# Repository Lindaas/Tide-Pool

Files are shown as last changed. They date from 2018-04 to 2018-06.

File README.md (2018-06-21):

# Tide-Pool
**This repository contains the code to run the tide pool
for the marine lab biology group.**

## Table of Contents
1. [Description](#Description)
2. [Installation](#Installation)
3. [Code Discussion](#Code-Discussion)
4. [Credit](#credit)

## Description
This code controls the pumping system for both the tide pool and the stingray
lagoon. There are currently two pumps that when one is on, it empties the tank
it is in filling the other tank.

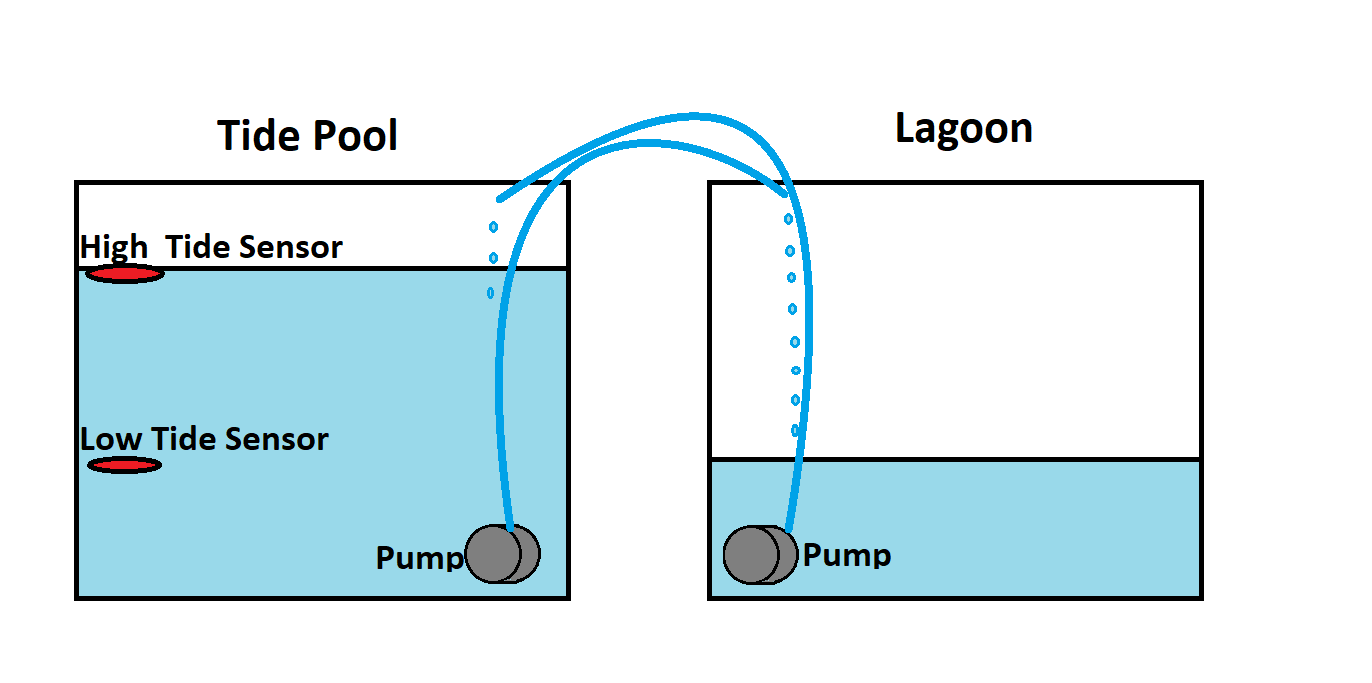
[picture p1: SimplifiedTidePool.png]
Simplified Tide Pool Diagram


Currently, the tide pool and lagoon oscillate between high and low tide every six and a half hours. The system wants the tide pool to be at high tide when the lagoon is at low tide and vice versa. When the [Arduino program](TidePoolLCD/TidePoolLCD.ino) starts, the tide pool fills with water from the lagoon. This filling by turning the pump off for five minutes and then turning it on for the next five minutes repeats until the high tide sensor is triggered. If for some reason the water level decreases, the pump will fill again until the high tide sensor is on. After six and a half hours passed, the system then will pump water from the tide pool into the lagoon until the tide pool's low tide sensor is triggered. After six and a half hours pass, the pump to fill the tide pool turns on and this tidal system repeats.

This system is connected to hardware that connects it to Wi-Fi called the Adafruit Huzzah ESP8266 Breakout Board. This system gets the height values from the ultrasonic sensor that the Arduino records. These values are then sent to Adafruit io, a free online tool. The levels are recorded every three seconds and are kept for a month and can be found at [Adafruit IO Online Dashboard](https://io.adafruit.com/anonymousAlligator/dashboards/ultrasonicsensordashboard). If the Arduino stops, the data isn't sent to Adafruit io and an email notification is sent within 30 minutes.

The schematic for the current system looks like the below image:
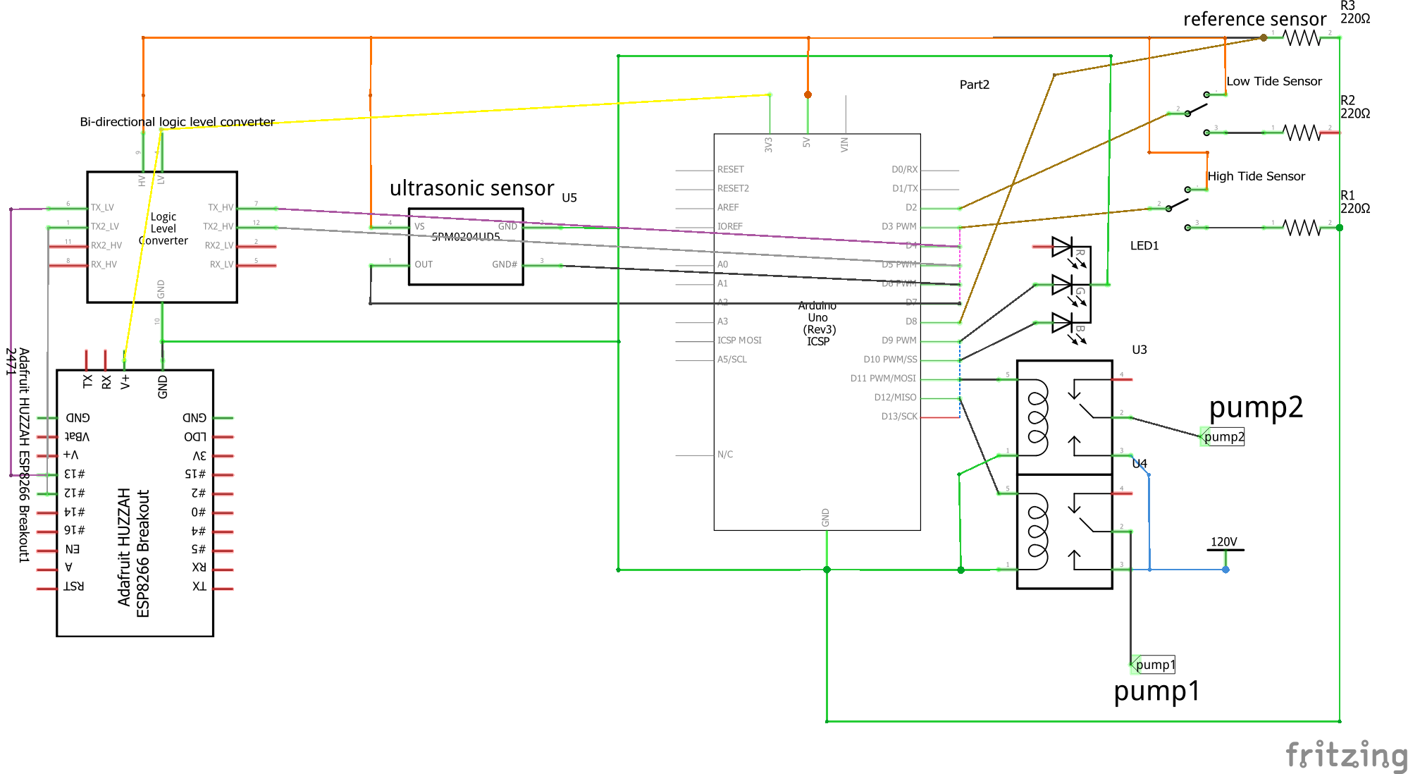
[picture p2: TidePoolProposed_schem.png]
Tide Pool Schematic


**Soon to be implemented** the tidal data will be pulled from online and will mimic the tidal predictions from Kiptopeke, VA.

## Installation
1. Download the [Arduino IDE](https://www.arduino.cc/en/Main/Software?) or preferred Arduino editor.
2. Clone the repository `git clone https://github.com/meyerpa/Tide-Pool.git`
3. Upload https://github.com/meyerpa/Tide-Pool/blob/master/TidePoolLCD/TidePoolLCD.ino to an Arduino.
4. [Create an Adafruit IO Account](https://accounts.adafruit.com/users/sign_up). If need help figuring out how use it, follow the [adafruit io getting started guide](https://learn.adafruit.com/mqtt-adafruit-io-and-you/getting-started-on-adafruit-io)
5. Update `IO_USERNAME`, `IO_KEY`, `WIFI_SSID` (Wi-Fi Network Name), and `WIFI_PASS` (Wi-Fi Password), in `ESP8266/config.h` then upload https://github.com/meyerpa/Tide-Pool/tree/master/ESP8266 to the Adafruit ESP8266 Huzzah Board.
6. Connect the hardware as shown in the below schematic above Installation.

## Components
**SunFounder 2 Channel Relay**

Image of the 2 Channel Relay

The relay allows the Arduino Uno to switch the pumps on and off as necessary.  The Arduino is a low voltage and low amperage system and cannot supply enough power to operate the pumps.  The relay functions like a switch and you should hear a “click” when a pump switches on or off, which also turn one of two red lights located on the rear of the device.
[*URL*](http://www.amazon.com/SunFounder-Channel-Shield-Arduino-Raspberry/dp/B00E0NTPP4/ref=sr_1_2?ie=UTF8&qid=1436551285&sr=8-2&keywords=relay+arduino)

The Arduino and the relay should be connected as follows:

|Arduino	| Relay |
|---------|-------|
| GND	    | GND   |
| 5V	    |	VCC   |
| 11    	| IN1   |
|12	      | IN2   |

**Arduino Uno - Microcontroller**

Image of the Arduino Uno

The Arduino acts like the brain of the system.  It talks to the relay to turn the pumps on and off based on the code that is programmed into the controller.  Only 14 of the pins (labeled: GND, 5V, 3.3V, 2, 3, 4, 5, 6, 7, 8, 9, 10, 11, and 12) should be in use.
The USB cord is used to upload code from a computer to the Arduino and may remain connected to the board.  The last connection to the board is the power supply (looks similar to a phone charger), which will have to power the Arduino at all, time and the charger should have a red light to indicate that it is on.  The Arduino should have a green light to indicate that it is receiving power that is located on the opposite side as the USB port.
[*URL*](http://www.amazon.com/Atmega328p-Atmega16u2-Version-Board-Arduino/dp/B00SF28U7A/ref=sr_1_8?ie=UTF8&qid=1436553628&sr=8-8&keywords=arduino)

**Grove Seeed RGB LCD**

Image of RGB LCD

This LCD (Liquid Crystal Display) shows the system’s current state—filling or draining. It also shows whether the high or low tide bobbers are triggered. If the bobbers are both triggered, the system is in an error state.
[*URL*](http://wiki.seeedstudio.com/Grove-LCD_RGB_Backlight/)

**Grove Seeed Base Shield V2**

Image of Grove Seeed Base Shield V2

This shield allows the RGB LCD to easily communicate with the Arduino.
[*URL*](http://wiki.seeedstudio.com/Base_Shield_V2/)

**Ultrasonic Sensor HC-SR04**

Image of Ultrasonic Sensor

This sensor can read the exact water level. This sensor reads in the exact tidal level. This sensor sends the tidal level readings to the Wi-Fi ESP8266 chip.
[*URL*](https://www.sparkfun.com/products/13959)

**Bi-directional Logic Converter**

Image of Bi-directional Logic Converter

This chip converts the Arduino’s 5 Volt digital output pins to a 3 Volt level able to be read by the Wi-Fi chip. This is because the Wi-Fi chip operates on a 3 Volt logic level, while the Arduino operates on a 5 Volt logic level. If the Arduino is incorrectly connected to the Wi-Fi chip without the logic converter, the Wi-Fi chip could break.
[*URL*](https://www.sparkfun.com/products/12009)

**Wi-Fi Chip (Adafruit ESP8266 Huzzah Breakout Board)**

Image of Adafruit ESP8266 Huzzah Breakout Board

This chip is connected to a wireless network. This enables the project to send the tidal readings to an online source. The current online source the tidal data is pushed to is Adafruit io. This online source accepts data every three seconds, and will send an email after thirty minutes if the system is halted. This chip gets readings from the Arduino via a serial connection on pin 12 (receiving RX) and pin 13 (transmitting TX) and sends that information to the Adafruit io system to be logged for a month.
[*URL*](https://learn.adafruit.com/adafruit-huzzah-esp8266-breakout/overview)

**High Tide Switch/Bobber**

Image of High Tide Switch/Bobber

This switch tells whether the tide is high or low. This bobber switches the fill pump off after the pump has been on for the minimum five-minute time.
[*URL*](https://www.amazon.com/uxcell-Pieces-ZP4510-Vertical-Switches/dp/B00FHAEBIA/ref=sr_1_2?ie=UTF8&qid=1529595162&sr=8-2&keywords=arduino+float+switch)

**Low Tide Switch/Bobber**

Image of Low Tide Switch/Bobber

This switch tells whether the tide is high or low. This bobber switches the drain pump off after the pump has been on for the minimum five-minute time.
[*URL*](https://www.amazon.com/uxcell-Pieces-ZP4510-Vertical-Switches/dp/B00FHAEBIA/ref=sr_1_2?ie=UTF8&qid=1529595162&sr=8-2&keywords=arduino+float+switch)

**Saltwater Pump (2)**

Image of Saltwater Pump

These two pumps do not operate at the same head and the head “velocity” will very over time between the two they pump at different rates.  These pumps are connected to an outlet, which turns on the pumps through the relay. This means that even though the pumps may look like they are plugged in, the outlet may be “off”.
[*URL*](https://www.drsfostersmith.com/product/prod_display.cfm?c=3578+4587+21413&pcatid=21413)

**Waterproof Hobby Box**

Image of Waterproof Hobby Box

This is a box that keeps the electrical components dry.  There were some issues (minor shock) due to the hobby box not being waterproof and corrosive saltwater vapor.  Make sure that if the box is opened that the cords that are fed into the box rest between the jell sealant and that the box clasps are properly fastened.  If a replacement is needed make sure to purchase a large one.
[*URL*](http://www.amazon.com/Weatherproof-Outdoor-Electrical-Connection-Enclosure/dp/B006EUHRK6/ref=sr_1_fkmr3_1?ie=UTF8&qid=1431288296&sr=8-1-fkmr3&keywords=waterproof+electrical+hobby+box)

## Code Discussion 
The code has two components:
1. [The  Arduino part that controls the motors](https://github.com/meyerpa/Tide-Pool/blob/master/TidePoolLCD/TidePoolLCD.ino)
2. [The Wi-Fi Chip Part that uploads the tidal level](https://github.com/meyerpa/Tide-Pool/tree/master/ESP8266)

The Arduino is running this current code.

The code requires input from sensors. There are two sensors to detect extreme tidal level. One sensor detects high tide and the other sensor detects low tide. The tide switches from high to low and vice versa every 6.5 hours.

The Arduino controls the pumps through a relay. The Arduino will either be in a state of filling or draining the tide pool. The fill and drain will continue until the high or low tide sensors are toggled, respectively. When the tide pool is filling, the fill pump will either be one or off. The pump is initially off for five minutes and then will turn on for the next five minutes. The following five minutes the pump will be off. This pattern continues until the high tide bobber is toggled on. A similar pattern happens with the drain pump until the low tide bobber is toggled on.

This system functions by itself filling and draining the tide pool. But there is an additional system to send the tide level online, so the system can be monitored. This additional system has a ultrasonic sensor to detect the exact water (tidal) level. This sensor observes the tidal level and sends the level online by serially communicating to the Wi-Fi chip which sends the level to the [Adafruit IO Online Feed](https://io.adafruit.com/anonymousAlligator/feeds/ultrasonicsensor).

## Credit 
[Dr. Steve Lindaas](mailto:lindaas@mnstate.edu),
[Paige Meyer](mailto:paigemey7@gmail.com), or
[Benjamin LeMay](benjaminlemay@protonmail.com)

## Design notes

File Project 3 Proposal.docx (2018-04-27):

# Project 3

Paige Meyer

# Objective

I first propose to update the tide pool’s pumping system in the marine lab to make it safer. The way I would like to make the pumping system more safe is to have the pumps grounded when off as opposed to the current high voltage when off, and ungrounded. I will also like to make the system more understandable to diagnose by adding a LCD screen to state whether the left tank is tidally filling, still, or falling. I also propose to add either shrink-wrap or electrical tape to the uninsulated wire connections to avoid unintentional short circuits in the future.

I secondly propose to use ultrasonic sensors to the pump system. These ultrasonic sensors will be located high above the tank, to avoid splash failures. These sensitive sensors will enable a more precise control of the water level. This precise control will enable the tide pool to mock Chesapeake Bay’s tides.

The third part of the project will be to connect a Wi-Fi module to the pumping system; this will enable the pool to access the up-to-date Chesapeake tide from an online database. This query will allow realistic tidal simulations in our current marine lab.

The fourth and last part of the project I propose to do is to have the system send an email to the marine lab group when a sensor fails, to inform them of the failure and correct the failure. I would also like to create a webpage that shows the current tide level in the marine lab alongside the Chesapeake Bay actual tide levels.

# Project Design

## Schematic

The initial, starting schematic is shown in Figure 1.

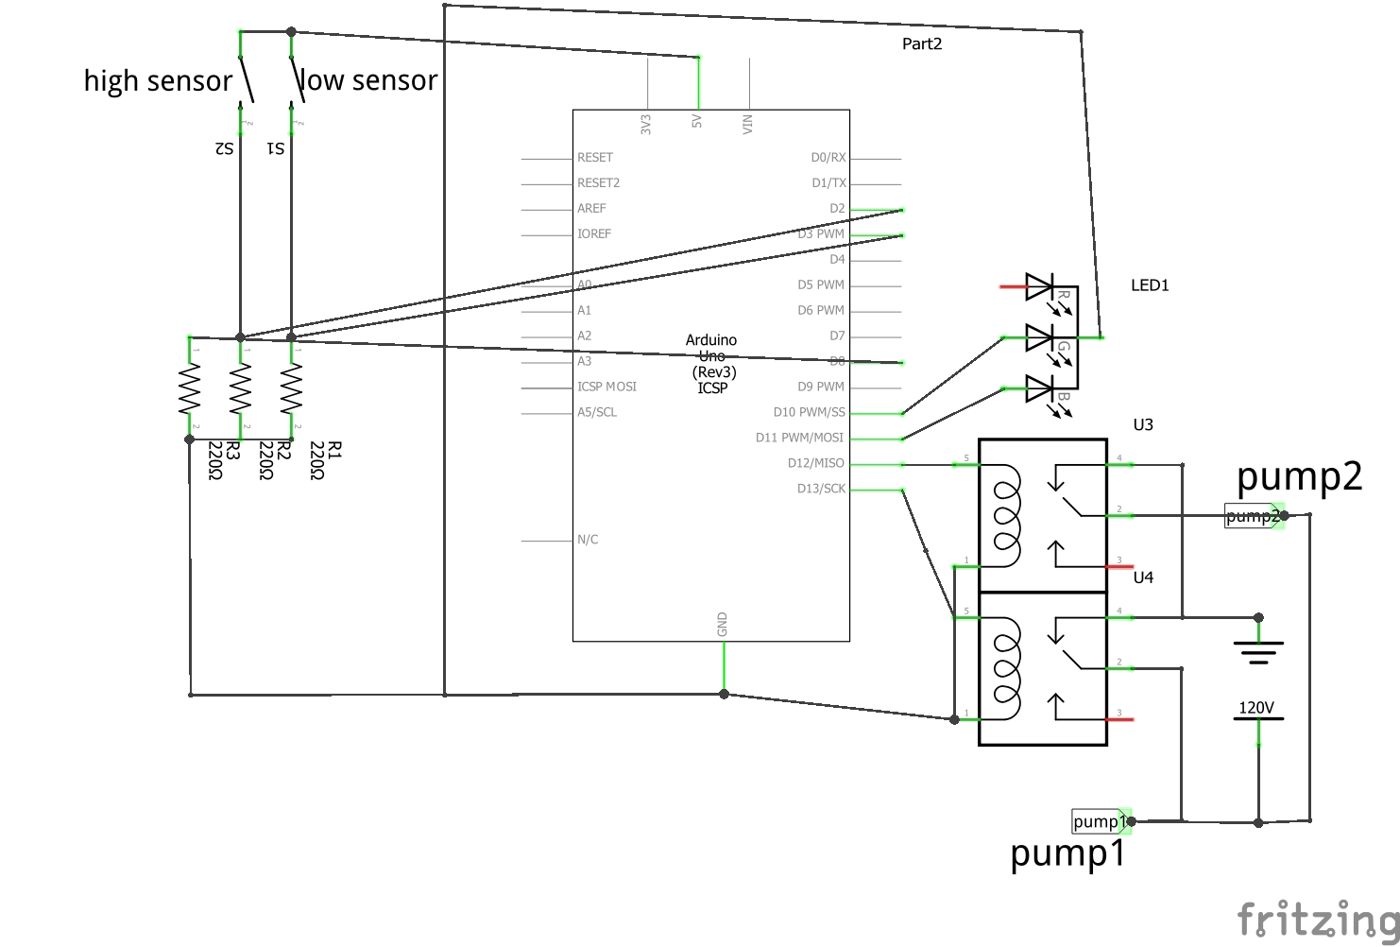
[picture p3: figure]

Figure 1-Initial Starting Schematic

My proposed schematic would look like Figure 2.

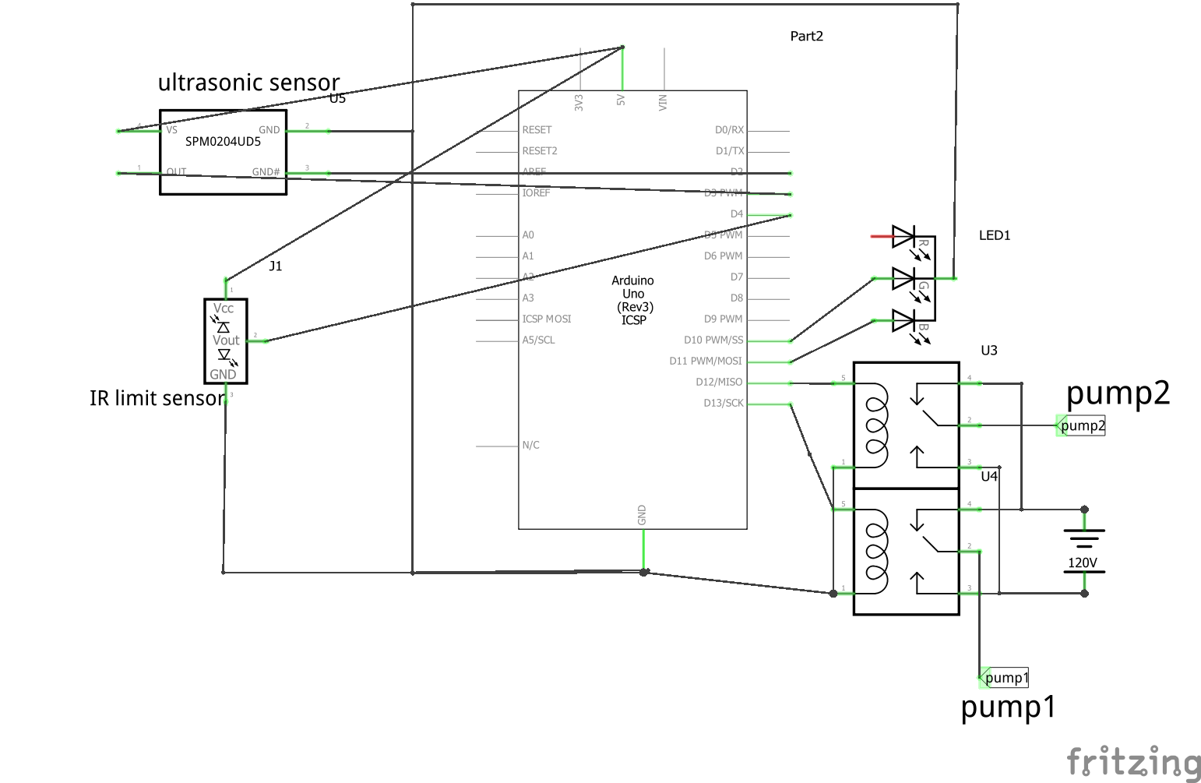
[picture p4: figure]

Figure 2-Proposed Schematic

## Detailed Analysis of the proposed circuit

### Power supply design

The power supply for the circuit is provided by either the Arduino or the wall outlet. The Arduino’s power supply should be a DC adapter that provides between 9 and 12 Volts DC, 250 mA or more, 2.1mm plug, and the center pin should be positive [1].

The power supply each pump should be wall, outlet voltage. The wall outlet hanging down in the marine lab provides 120 Volt RMS AC current to the two outlets inside of the black, waterproof container. I need to ensure that these two outlets are connected in parallel so they each get 120 Volts RMS even when both pumps are on.

### Sensor States

For the high and low sensors, these are the limit switches. If the water is lower than the low sensor, we know not to pump any more water out of the tank. When the high sensor is triggered, water is above the high sensor and we know not to pump any more water into the take. We know that these sensors have the tendency to fail over time, so the ultrasonic sensor will be used as the truth, and can email to notify the marine lab participants when the high and low sensor are triggered.

Ultrasonic sensors can read the distance to the water. These will read in a number from 0 to 1023. This number will be translated to the distance of the object in inches by scaling the duration for the ultrasonic wave to travel back. The equation is as follows:

distanceInch = (duration*0.0133)/2.

This will be compared to the height the water should be and a pump will drain/fill or stop draining/filling.

### Power Consumption

The major power-consuming components would be the pumps. The new pump, model Pump 320, consumes 23 Watts when it is on. I’m not exactly sure about the other pump, but let’s assume it is similar to this pump, and consumes 23 Watts when it is on as well. Estimating the each pump will be on 4 hours each day. This means that each pump consumes 0.023 kilowatts. This means that both pumps consume 0.023 kilowatts + 0.023 kilowatts = 0.046 kilowatts when running. Finding the kilowatt-hours, we use 0.046 kilowatts x 4 hours = 0.184 kWh per day. Doing this everyday, we find the circuit uses about 0.184 kWh per day * 365 days = 67.16 kWh per year.

### Max Power Dissipation

The pumps are rated to ___ Volts. [Need to look up to make sure not delivering too much power].

### Parts identification

2 Relay Module SRD-05VDC-SL-C

Arduino Uno

Wi-Fi Breakout Board HUZZAH ESP8266Mod AI-Thinker

Grove-LCD RGB Backlight V2.0

Ultrasonic Sensors HC-SR04

Tri-color LED unsure about part number

Pump 2 Hydor Universal Pump 320 (Seltz L30)

Pump 1 Lifegard Aquatics ARP440110 Quiet One Aquarium 2200

### Optimization

I may want to use multiple (three) ultrasonic sensors, as one may fail and cause a catastrophic failure. If one is consistently different from the others, a notification can be sent about replacing the ultrasonic sensor.

I hope that I will be able to connect the tide pool to a website, because that may be a good visual for people who come into the lab to see. Eventually, the television in the marine lab may be able to show the last month’s tides in the pool. That may be a good way to explain how tides do not always go from extreme values.

# References

[1] Arduino Playground. What Adapter (2018).

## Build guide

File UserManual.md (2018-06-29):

# User Manual

## System Overview

Currently, the tide pool and lagoon oscillate between high and low tide every six and a half hours. The system wants the tide pool to be at high tide when the lagoon is at low tide and vice versa. When the [arduino program](TidePoolLCD/TidePoolLCD.ino) starts, the tide pool fills with water from the lagoon. This filling by turning the pump off for five minutes and then turning it on for the next five minutes repeats until the high tide sensor is triggered. **There is a delay of the remaining five minutes that the pump is on for the pump to turn off and the LCD screen to update. This is so the pumps don't cycle on and off too quickly.** If for some reason the water level decreases, the pump will fill again until the high tide sensor is on. After six and a half hours passed, the system then will pump water from the tide pool into the lagoon until the tide pool's low tide sensor is triggered. After six and a half hours pass, the pump to fill the tide pool turns on and this tidal system repeats.

This system is connected to hardware that connects it to Wi-Fi called the Adafruit Huzzah ESP8266 Breakout Board. This system gets the height values from the ultrasonic sensor that the Arduino records. These values are then sent to Adafruit io, a free online tool. The levels are recorded every three seconds and are kept for a month and can be found at [Adafruit IO Online Dashboard](https://io.adafruit.com/anonymousAlligator/dashboards/ultrasonicsensordashboard). If the Arduino stops, the data isn't sent to Adafruit io for an hour, an email notification is sent.

## Outputs
### LCD Screen
Currently, the LCD Screen has two rows, the top row prints the current state.
The current state may be any of the following:

| State Message | Meaning |
| ------- | ------- |
| Tide Pool Full | The tide pool finished filling and switches over to draining |
| Filling Tidepool | This is displayed in the 5 minute interval of where the pump filling the tide pool is on |
| Pause Filling Tide | This is displayed in the 5 minute interval where the fill pump turns off, to slow the fill cycle |
| Stop fill high tide | The high tide sensor is triggered, so the fill pump is turned off |
| Tide Pool Drained | The tide pool finished the 6.5 hour draining cycle and will now switch to filling the tide pool |
| Draining Tidepool | This is displayed in the 5 minute interval where the pump to drain the tide pool is on |
| Pause Draining Tide | This is displayed in the 5 minute interval where the drain pump turns off, slowing down the drain cycle |
| Stop fill low tide | The low tide sensor is triggered, so the drain pump is turned off |

The second row of the LCD displays the current sensor states

| Message | Meaning |
| ------- | ------- |
|         | The tide pool water level neither low or high |
| LOW TIDE | The tide pool water level is below the low water sensor |
| HIGH TIDE | The tide pool water level is above the high water sensor |
| SENSOR ERROR | Both low and high tide is detected. This should be impossible, and indicates one of the sensors is not working |

## LED indicator
The second way to tell whether the Arduino is working is by looking at the LED
light in the black container. This LED blinks fast (every 0.2 seconds) if a
pump should be on. The LED blinks slow if both pumps should be off. If the LED
is not blinking, at the high or low tide sensor is on. The color of the light
indicates whether the tide pool is filling or draining

| Color | Meaning |
| ----- | ------- |
| Blue  | The tide pool is draining see the above paragraph if the pump should be on or not |
| Green | The tide pool is filling  see the above paragraph if the pump should be on or not |

## Stuff isn't working
A good way of fixing most issues is to restart the Arduino and/or the Wi-Fi board. The way to reset these are pictured in the below text. In addition, there are some ways of diagnosing issues included below.

 **Problem: The online log isn't updating.**
 **Cause:** this could have multiple causes. I need you to do a few things to help figure out what the cause could be.
1. First, try flipping the high or low tide sensor. If the LCD screen doesn't change color when the sensor is flipped, the Arduino is halted. Restart the Arduino by pressing the reset button pictured below. If the green LED doesn't light up when the button is pressed, go to step 5. If the LCD screen updated when the sensor if flipped, proceed to 2.
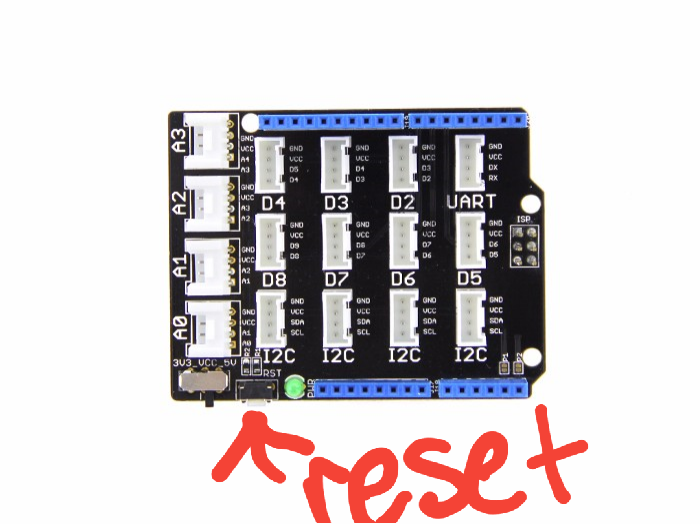
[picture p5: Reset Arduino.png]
Image of Grove Seeed Base Shield V2 Reset Button

2. The Arduino is running fine. This means that it could be a problem either with the ultrasonic sensor detecting a distance of 0 or with the Wi-Fi chip not connecting to the Adafruit IO website properly. Try resetting the Wi-Fi chip by pressing the button indicated in the image below. If the red and blue LCDs doesn't light up when reset, go to step 6. This chip could have lost connectivity to the wireless network. Wait two minutes and check the feed. If the feed is still not updating, go to 3.
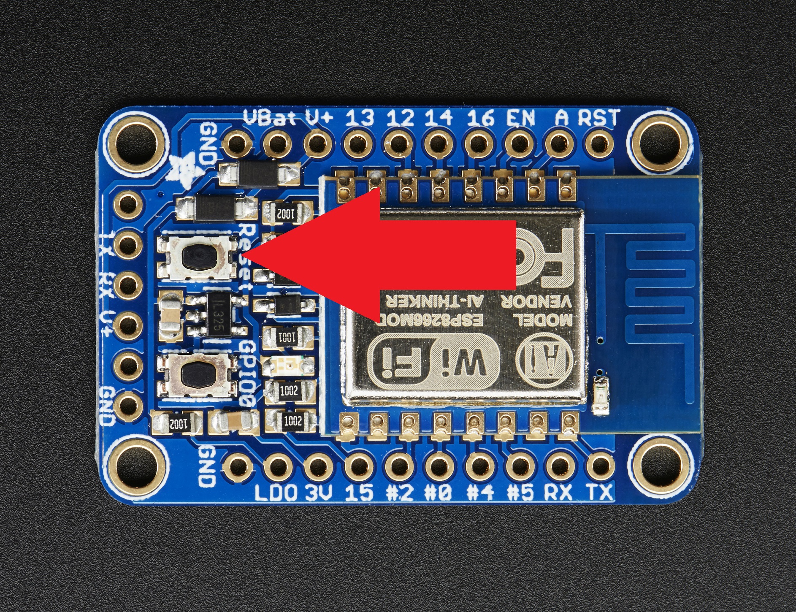
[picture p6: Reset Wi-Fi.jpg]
Image of Adafruit Huzzah ESP8266 Reset Button

3. Replace the ultrasonic sensor with a new one. The environment we are working in is corrosive to the sensor, and the sensor could be broken. If this doesn't
fix the issue proceed to step 4.
4. Make sure all of the connections are correct. The pins should be connected as follows:

| Arduino | Ultrasonic Sensor |
| ------- | ----------------- |
| 5V | Vcc |
| Gnd | Gnd |
| 6 | Trig |
| 7 | Echo |

5. Ensure the Arduino's power adapter is plugged in and the red LED is illuminated. If there still isn't any power, go to step 7.

6. Ensure that the Wi-Fi chip is plugged in and connected correctly. Make sure the Serial cable's black wire is connected to ground and is plugged in to the tan power strip. The Wi-Fi chip should be connected to the Bi-directional logic converter as follows:

| Logic Converter | Wi-Fi Chip |
| --- | --- |
| LV | V+ |
| GND | GND |
| LV1 | 13 |
| LV2 | 12 |

Then the Logic Converter chip should be connected to the Arduino as follows:

| Arduino | Logic Converter |
| --- | --- |
| 5V | HV |
| Gnd | GND |
| HV1 | 4 |
| HV2 | 5 |

7. Ensure the power strip is turned on. Make sure that the tan power strip red button is flipped to RESET. Still not working? Go to step 8.

8. Make sure the GFCI outlet is powered on. This outlet is outside the waterproof box. It powers the power strip. Make sure the green light on this is on. If it is not, reset it. If the power still doesn't turn on, the breaker outside the room may need to be flipped.

**Problem: The online log says the tide has been high or low for over 6 hours**
**Cause:** The drain pump is not getting turned on. Do the following steps
1. Make sure the relay is plugged powered on and is connected incorrectly. The Arduino's pin and the relay should be connected as follows:

| Arduino | Relay |
| ------- | ----- |
| 5V | Vcc |
| 12 | IN1 |
| 11 | IN2 |
| GND | Gnd |

**Problem: The high or low sensor is stuck**
**Cause:** First make sure, the white bobbers are clean and can easily slide. Second, make sure the connections are correct. Check that pins 2 and 3 are connected to the wire stands in the brown breadboard. Also, make sure below each resistor, the ground is connected properly.

**Problem: The distance seems to be messed up**
**Cause:** The ultrasonic sensor could be connected improperly or could be corroded. Try replacing the ultrasonic sensor inside the white 4" PVC pipe by disconnecting the wires and plugging in a new ultrasonic sensor. If the readings are still faulty, make sure the ultrasonic sensor is connected properly:

| Arduino | Ultrasonic Sensor |
| ------- | ----------------- |
| 5V | Vcc |
| Gnd | Gnd |
| 6 | Trig |
| 7 | Echo |

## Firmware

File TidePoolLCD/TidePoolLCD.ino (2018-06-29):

/*
  Tidepool

  This program will take the inputs from two switches and control indicator
  lights as well as pumps.  We want to have the time between low and high tide
  roughly 6.5 hours.  We don't know exactly how long it will take the little
  pumps to fill or drain.  So we will cycle them on/off and record the final time
  and then stay at high or low tide until 6.5 hours is reached.

  You can change the default of whether the tide is rising when the microcontroller
  first initializes.

  The goal is to simulate a tidal cycle (~13 hours)

  Inputs ---
  Pin 2: Lower switch +5V means water is too low
  Pin 3: High switch +5V means water is too high

  Pin 8: Reference (+5 V)

  Outputs ---
  Pin 09: Blue LED turn on when high switch is selected
  Pint 10: Green LED turn on when low switch is selected

  Pin 11: Relay IN2 = Left switch with infow pump (raising)
  Pin 12: Relay IN1 = Right switch with outflow pump (lowering)


  Author: Steve Lindaas - based on circuit and original program idea by Ben LeMay
  Version 1.0 April 9 2018
  Additional Author: Paige Meyer
  Version 1.3 April 10 2018
*/

#include <Wire.h>
#include "rgb_lcd.h"
#include <SoftwareSerial.h>
//#include <MemoryUsage.h>

rgb_lcd lcd;

boolean start;

// Pin constants won't change.

// high and low bobbers
const int InHigh =  3;
const int InLow  =  2;

// ultrasonic sensor pins
const int triggerPin = 6;
const int echoPin = 7;

// reference voltage pin
const int InRef  = 8;

// LEDs to show on or off
const int HighLED = 9;
const int LowLED  = 10;

// pins to communicate with the Wi-Fi Breakout Board
const int rxESPPin = 4;
const int txESPPin = 5;

// NOTE: Don't have any on pin 13 as this pin goes high when reset
const int PumpFill = 11;    // This pump fills the pool
const int PumpDrain = 12;   // This pump empties the pool

// Generally, use "unsigned long" for variables that hold time
// since the value will quickly become too large for an int to store
unsigned long startTime = 0;                        // store the tide half-cycle starting time
unsigned long previousTime = 0;                     // store the time since the pump was either turned on or off.

const unsigned long TideInterval = 6.5 * 60 * 60 * 1000;    // 6.5 hours is the half-period of a tide (in msec)
const unsigned long pumpOnTime = 5.0 * 60 * 1000;           // Pump is ON for 5 minutes
const unsigned long pumpOffTime = 6.1 * 60 * 1000;          // Pump is OFF for 6.1 minutes

// Tide state variables
boolean HighTide = false;          // Default lowering tide when you first turn on the system
boolean LowTide = false;
boolean Rising = false;
boolean PumpOn = true;

// variables to write about pump on
// These are used because they are the opposite of what most people would expect
const int writePumpOn = LOW;     // When pump is on, write low
const int writePumpOff = HIGH;   // When pump is off, write high

// Sensor varialbles - Initially set all the switches LOW (not tripped)
int sensorHigh = LOW;
int sensorLow = LOW;
int sensorRef = LOW;

// Set the last sensor states
int lastSensorHigh = sensorHigh;
int lastSensorLow = sensorLow;
int lastSensorRef = sensorRef;
unsigned long lastTimeHigh = 0;
unsigned long lastTimeLow = 0;
unsigned long lastTimeRef = 0;
unsigned long lastTimePulseHigh = 0;
unsigned long lastTimeLCDUpdated = 0;

const unsigned long debounceDelay = 100;
const unsigned long pulseDelay = 1000;       // delay a second before triggering the ultrasonic sensor
const unsigned long lcdDelay = 500;           // delay a half of a second between LCD updates

// Indicator light variables
unsigned long timeLED = 0;
int stateLED = LOW;             // ledState used to set the LED
long blinkLED = 500;           // interval at which to blink (milliseconds)
const long blinkFast = 150;
const long blinkSlow = 1000;

// ultrasonic sensor variables
unsigned long lastTimeUpdated = 0;
short delayUpdate = 3000;               // update only every 3000 milliseconds (3 seconds)

SoftwareSerial WiFiESP(rxESPPin, txESPPin);       // add fake serial ports to Wi-Fi board

// Tidal Level Data
//int currentTideIndex = 0;           // current index in tideLevels
//const int tideLevelLength = 7471;   // lenght of tide Level array
// const int timeBetween = 6 * 60 * 1000; // 6 minute tidal level interval
// const short tideLevels[] = {-0.01, -0.02, -0.02, -0.03, -0.03, -0.03, -0.03, -0.03, -0.03, -0.03, -0.02, -0.02, -0.01, -0.01, 0, 0.01, 0.02, 0.03, 0.05, 0.06, 0.07, 0.09, 0.11, 0.12, 0.14, 0.16, 0.18, 0.2, 0.22, 0.24, 0.27, 0.29, 0.31, 0.34, 0.36, 0.39, 0.41, 0.43, 0.46, 0.48, 0.51, 0.53, 0.55, 0.58, 0.6, 0.62, 0.64, 0.66, 0.68, 0.7, 0.72, 0.73, 0.75, 0.77, 0.78, 0.8, 0.81, 0.82, 0.83, 0.84, 0.85, 0.86, 0.87, 0.87, 0.88, 0.88, 0.89, 0.89, 0.89, 0.89, 0.89, 0.89, 0.89, 0.89, 0.88, 0.88, 0.87, 0.87, 0.86, 0.85, 0.84, 0.83, 0.82, 0.81, 0.79, 0.78, 0.76, 0.75, 0.73, 0.71, 0.69, 0.67, 0.65, 0.63, 0.61, 0.59, 0.57, 0.55, 0.52, 0.5, 0.48, 0.45, 0.43, 0.41, 0.38, 0.36, 0.34, 0.32, 0.29, 0.27, 0.25, 0.23, 0.21, 0.19, 0.17, 0.15, 0.13, 0.12, 0.1, 0.09, 0.07, 0.06, 0.04, 0.03, 0.02, 0.01, 0, -0.01, -0.01, -0.02, -0.02, -0.03, -0.03, -0.03, -0.03, -0.03, -0.03, -0.03, -0.02, -0.01, -0.01, 0, 0.01, 0.02, 0.03, 0.04, 0.06, 0.07, 0.09, 0.1, 0.12, 0.14, 0.16, 0.18, 0.2, 0.22, 0.25, 0.27, 0.29, 0.32, 0.34, 0.36, 0.39, 0.41, 0.44, 0.46, 0.48, 0.51, 0.53, 0.55, 0.57, 0.59, 0.61, 0.64, 0.66, 0.67, 0.69, 0.71, 0.72, 0.74, 0.75, 0.77, 0.78, 0.79, 0.8, 0.81, 0.82, 0.83, 0.83, 0.84, 0.84, 0.85, 0.85, 0.85, 0.85, 0.85, 0.85, 0.85, 0.84, 0.84, 0.83, 0.83, 0.82, 0.81, 0.8, 0.79, 0.78, 0.77, 0.75, 0.74, 0.72, 0.7, 0.69, 0.67, 0.65, 0.63, 0.61, 0.59, 0.56, 0.54, 0.52, 0.5, 0.47, 0.45, 0.42, 0.4, 0.38, 0.35, 0.33, 0.3, 0.28, 0.26, 0.23, 0.21, 0.19, 0.17, 0.15, 0.13, 0.11, 0.09, 0.07, 0.06, 0.04, 0.03, 0.01, 0, -0.01, -0.02, -0.03, -0.04, -0.05, -0.05, -0.06, -0.06, -0.07, -0.07, -0.07, -0.07, -0.07, -0.07, -0.06, -0.06, -0.05, -0.04, -0.03, -0.02, -0.01, 0, 0.02, 0.03, 0.05, 0.06, 0.08, 0.1, 0.12, 0.14, 0.17, 0.19, 0.21, 0.23, 0.26, 0.28, 0.31, 0.34, 0.36, 0.39, 0.41, 0.44, 0.46, 0.49, 0.52, 0.54, 0.56, 0.59, 0.61, 0.63, 0.66, 0.68, 0.7, 0.72, 0.74, 0.76, 0.77, 0.79, 0.8, 0.82, 0.83, 0.84, 0.86, 0.87, 0.88, 0.88, 0.89, 0.9, 0.9, 0.91, 0.91, 0.91, 0.92, 0.92, 0.91, 0.91, 0.91, 0.91, 0.9, 0.89, 0.89, 0.88, 0.87, 0.86, 0.85, 0.83, 0.82, 0.81, 0.79, 0.77, 0.76, 0.74, 0.72, 0.7, 0.68, 0.66, 0.63, 0.61, 0.59, 0.56, 0.54, 0.51, 0.49, 0.46, 0.44, 0.41, 0.39, 0.36, 0.34, 0.32, 0.29, 0.27, 0.24, 0.22, 0.2, 0.18, 0.16, 0.14, 0.12, 0.1, 0.08, 0.07, 0.05, 0.04, 0.02, 0.01, 0, -0.01, -0.03, -0.03, -0.04, -0.05, -0.05, -0.06, -0.06, -0.06, -0.06, -0.06, -0.06, -0.06, -0.05, -0.05, -0.04, -0.03, -0.02, -0.01, 0, 0.01, 0.03, 0.04, 0.06, 0.08, 0.1, 0.12, 0.14, 0.16, 0.18, 0.2, 0.23, 0.25, 0.28, 0.3, 0.33, 0.36, 0.38, 0.41, 0.43, 0.46, 0.49, 0.51, 0.54, 0.56, 0.59, 0.61, 0.63, 0.66, 0.68, 0.7, 0.72, 0.74, 0.75, 0.77, 0.79, 0.8, 0.82, 0.83, 0.84, 0.85, 0.86, 0.87, 0.88, 0.89, 0.89, 0.9, 0.9, 0.91, 0.91, 0.91, 0.91, 0.9, 0.9, 0.9, 0.89, 0.89, 0.88, 0.87, 0.86, 0.85, 0.83, 0.82, 0.81, 0.79, 0.78, 0.76, 0.74, 0.72, 0.7, 0.68, 0.66, 0.63, 0.61, 0.58, 0.56, 0.54, 0.51, 0.48, 0.46, 0.43, 0.41, 0.38, 0.35, 0.33, 0.3, 0.28, 0.25, 0.23, 0.2, 0.18, 0.16, 0.14, 0.12, 0.1, 0.08, 0.06, 0.04, 0.02, 0.01, -0.01, -0.02, -0.03, -0.05, -0.06, -0.07, -0.07, -0.08, -0.09, -0.09, -0.1, -0.1, -0.1, -0.1, -0.1, -0.09, -0.09, -0.08, -0.08, -0.07, -0.06, -0.05, -0.04, -0.02, -0.01, 0.01, 0.03, 0.04, 0.06, 0.08, 0.1, 0.13, 0.15, 0.17, 0.2, 0.22, 0.25, 0.28, 0.3, 0.33, 0.36, 0.38, 0.41, 0.44, 0.46, 0.49, 0.52, 0.54, 0.57, 0.59, 0.62, 0.64, 0.66, 0.69, 0.71, 0.73, 0.75, 0.77, 0.78, 0.8, 0.82, 0.83, 0.84, 0.86, 0.87, 0.88, 0.89, 0.9, 0.9, 0.91, 0.91, 0.92, 0.92, 0.92, 0.92, 0.92, 0.92, 0.92, 0.91, 0.91, 0.9, 0.9, 0.89, 0.88, 0.87, 0.85, 0.84, 0.83, 0.81, 0.8, 0.78, 0.76, 0.74, 0.72, 0.7, 0.68, 0.65, 0.63, 0.61, 0.58, 0.56, 0.53, 0.51, 0.48, 0.46, 0.43, 0.41, 0.38, 0.35, 0.33, 0.3, 0.28, 0.25, 0.23, 0.21, 0.18, 0.16, 0.14, 0.12, 0.1, 0.08, 0.06, 0.04, 0.03, 0.01, 0, -0.01, -0.03, -0.04, -0.05, -0.06, -0.06, -0.07, -0.07, -0.08, -0.08, -0.08, -0.08, -0.08, -0.08, -0.08, -0.07, -0.07, -0.06, -0.05, -0.04, -0.03, -0.01, 0, 0.02, 0.03, 0.05, 0.07, 0.09, 0.11, 0.14, 0.16, 0.18, 0.21, 0.23, 0.26, 0.28, 0.31, 0.34, 0.37, 0.39, 0.42, 0.45, 0.48, 0.5, 0.53, 0.56, 0.58, 0.61, 0.63, 0.66, 0.68, 0.7, 0.73, 0.75, 0.77, 0.79, 0.81, 0.82, 0.84, 0.85, 0.87, 0.88, 0.89, 0.9, 0.91, 0.92, 0.93, 0.93, 0.94, 0.94, 0.94, 0.95, 0.95, 0.94, 0.94, 0.94, 0.94, 0.93, 0.92, 0.91, 0.91, 0.89, 0.88, 0.87, 0.85, 0.84, 0.82, 0.81, 0.79, 0.77, 0.75, 0.73, 0.7, 0.68, 0.66, 0.63, 0.61, 0.58, 0.56, 0.53, 0.5, 0.48, 0.45, 0.42, 0.39, 0.37, 0.34, 0.31, 0.29, 0.26, 0.24, 0.21, 0.19, 0.16, 0.14, 0.12, 0.1, 0.08, 0.06, 0.04, 0.02, 0, -0.01, -0.03, -0.04, -0.05, -0.06, -0.07, -0.08, -0.09, -0.1, -0.1, -0.1, -0.11, -0.11, -0.11, -0.11, -0.1, -0.1, -0.1, -0.09, -0.08, -0.07, -0.06, -0.05, -0.04, -0.02, -0.01, 0.01, 0.03, 0.05, 0.07, 0.09, 0.11, 0.14, 0.16, 0.18, 0.21, 0.23, 0.26, 0.29, 0.32, 0.34, 0.37, 0.4, 0.42, 0.45, 0.48, 0.51, 0.53, 0.56, 0.58, 0.61, 0.63, 0.66, 0.68, 0.7, 0.72, 0.74, 0.76, 0.78, 0.79, 0.81, 0.82, 0.84, 0.85, 0.86, 0.87, 0.88, 0.89, 0.9, 0.9, 0.91, 0.91, 0.91, 0.91, 0.91, 0.91, 0.91, 0.91, 0.9, 0.9, 0.89, 0.88, 0.87, 0.86, 0.85, 0.84, 0.83, 0.81, 0.8, 0.78, 0.76, 0.74, 0.72, 0.7, 0.68, 0.66, 0.64, 0.61, 0.59, 0.56, 0.54, 0.51, 0.49, 0.46, 0.43, 0.41, 0.38, 0.36, 0.33, 0.31, 0.28, 0.26, 0.23, 0.21, 0.18, 0.16, 0.14, 0.12, 0.1, 0.08, 0.06, 0.05, 0.03, 0.01, 0, -0.01, -0.03, -0.04, -0.05, -0.06, -0.06, -0.07, -0.08, -0.08, -0.08, -0.08, -0.09, -0.08, -0.08, -0.08, -0.07, -0.07, -0.06, -0.05, -0.04, -0.03, -0.02, 0, 0.01, 0.03, 0.05, 0.07, 0.09, 0.11, 0.13, 0.15, 0.18, 0.2, 0.23, 0.25, 0.28, 0.31, 0.33, 0.36, 0.39, 0.42, 0.45, 0.47, 0.5, 0.53, 0.56, 0.58, 0.61, 0.64, 0.66, 0.69, 0.71, 0.73, 0.75, 0.78, 0.8, 0.81, 0.83, 0.85, 0.86, 0.88, 0.89, 0.91, 0.92, 0.93, 0.94, 0.94, 0.95, 0.96, 0.96, 0.96, 0.97, 0.97, 0.97, 0.96, 0.96, 0.96, 0.95, 0.94, 0.94, 0.93, 0.92, 0.91, 0.89, 0.88, 0.86, 0.85, 0.83, 0.81, 0.8, 0.78, 0.75, 0.73, 0.71, 0.69, 0.66, 0.64, 0.61, 0.59, 0.56, 0.53, 0.51, 0.48, 0.45, 0.42, 0.4, 0.37, 0.34, 0.32, 0.29, 0.26, 0.24, 0.21, 0.19, 0.17, 0.14, 0.12, 0.1, 0.08, 0.06, 0.04, 0.03, 0.01, -0.01, -0.02, -0.03, -0.05, -0.06, -0.07, -0.07, -0.08, -0.09, -0.09, -0.1, -0.1, -0.1, -0.1, -0.1, -0.1, -0.09, -0.09, -0.08, -0.07, -0.06, -0.05, -0.04, -0.03, -0.01, 0, 0.02, 0.04, 0.05, 0.07, 0.1, 0.12, 0.14, 0.16, 0.19, 0.21, 0.24, 0.26, 0.29, 0.32, 0.34, 0.37, 0.4, 0.42, 0.45, 0.48, 0.5, 0.53, 0.55, 0.58, 0.6, 0.63, 0.65, 0.67, 0.69, 0.71, 0.73, 0.75, 0.77, 0.78, 0.8, 0.81, 0.82, 0.83, 0.84, 0.85, 0.86, 0.87, 0.88, 0.88, 0.89, 0.89, 0.89, 0.89, 0.89, 0.89, 0.88, 0.88, 0.87, 0.87, 0.86, 0.85, 0.84, 0.83, 0.82, 0.81, 0.79, 0.78, 0.76, 0.74, 0.73, 0.71, 0.69, 0.67, 0.65, 0.62, 0.6, 0.58, 0.55, 0.53, 0.51, 0.48, 0.46, 0.43, 0.41, 0.38, 0.35, 0.33, 0.3, 0.28, 0.26, 0.23, 0.21, 0.19, 0.17, 0.14, 0.12, 0.11, 0.09, 0.07, 0.05, 0.04, 0.02, 0.01, 0, -0.01, -0.03, -0.04, -0.04, -0.05, -0.06, -0.06, -0.07, -0.07, -0.07, -0.07, -0.07, -0.07, -0.06, -0.06, -0.05, -0.04, -0.03, -0.02, -0.01, 0, 0.01, 0.03, 0.04, 0.06, 0.08, 0.1, 0.12, 0.14, 0.16, 0.19, 0.21, 0.24, 0.26, 0.29, 0.31, 0.34, 0.37, 0.4, 0.42, 0.45, 0.48, 0.51, 0.53, 0.56, 0.59, 0.61, 0.64, 0.66, 0.69, 0.71, 0.73, 0.76, 0.78, 0.8, 0.81, 0.83, 0.85, 0.87, 0.88, 0.89, 0.91, 0.92, 0.93, 0.94, 0.94, 0.95, 0.96, 0.96, 0.96, 0.96, 0.96, 0.96, 0.96, 0.96, 0.96, 0.95, 0.94, 0.94, 0.93, 0.92, 0.91, 0.9, 0.88, 0.87, 0.85, 0.84, 0.82, 0.8, 0.78, 0.76, 0.74, 0.72, 0.7, 0.67, 0.65, 0.62, 0.6, 0.57, 0.55, 0.52, 0.5, 0.47, 0.44, 0.42, 0.39, 0.36, 0.34, 0.31, 0.29, 0.26, 0.24, 0.22, 0.19, 0.17, 0.15, 0.13, 0.11, 0.09, 0.07, 0.05, 0.04, 0.02, 0.01, 0, -0.02, -0.03, -0.04, -0.05, -0.05, -0.06, -0.07, -0.07, -0.07, -0.07, -0.07, -0.07, -0.07, -0.07, -0.07, -0.06, -0.05, -0.04, -0.04, -0.03, -0.01, 0, 0.01, 0.03,
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

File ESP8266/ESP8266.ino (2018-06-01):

// Adafruit Feather HUZZAH esp8266 Code

#include <SoftwareSerial.h>
#include <ESP8266WiFi.h>
// edit the config.h tab and enter your Adafruit IO credentials
// and any additional configuration needed for WiFi, cellular,
// or ethernet clients.
#include "config.h"

#define rxPin 12
#define txPin 13
SoftwareSerial incoming(rxPin, txPin);
AdafruitIO_Feed *ultrasonicSensorFeed = io.feed("UltrasonicSensorFeed");

void setup() {
  pinMode(rxPin, INPUT);
  pinMode(txPin, OUTPUT);
  
  Serial.begin(9600);
  
  Serial.println();
  Serial.println("Serial begun.");
  incoming.begin(9600);

  

  Serial.print("Connecting to Adafruit IO");

  // connect to io.adafruit.com
  io.connect();

  // wait for a connection
  while(io.status() < AIO_CONNECTED) {
    Serial.print(".");
    delay(500);
  }

  // we are connected
  Serial.println();
  Serial.println(io.statusText());
  
#ifndef ESP8266
  while (!incoming);     // will pause Zero, Leonardo, etc until serial console opens  Serial.begin(115200);
#endif
  
}


void loop() {
  float distance;
  char letter;
  int i = 0;

  
  io.run();

  if (incoming.available()) {
    
    Serial.print("-");
    delay(10); //allows all serial sent to be received together
    distance = incoming.parseFloat();

    if (distance > 0) {
      Serial.print("Distance: ");
      Serial.println(distance);
    
      ultrasonicSensorFeed->save(distance);
    }
    
    //sendToWeb(message);
  }
}

/*
void sendToWeb(String mssg) {
  // Use WiFiClient class to create TCP connections
  WiFiClient client;
  const int httpPort = 80;
  if (!client.connect(host, httpPort)) {
    Serial.println("Connection failed!");
    return;
  }
  // Prep message for url arguement
  mssg.replace(" ", "+");
  mssg.replace("'", "%27");

  /*String request = "";
  request += "GET ";
  request += "/recordMssg.php?mssg=" + mssg;
  request += " HTTP/1.1\r\n";
  request += "Host: " ;
  request += host;
  request += "\r\nConnection: close\r\n\r\n";
  Serial.println(request);
  ultrasonicSensorFeed->save(mssg);
  /*client.print(request);
  delay(1000);
  while (client.available()) {
    String line = client.readStringUntil('\r');
    Serial.print(line);
  }*/

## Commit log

2018-04-21 Add Schematics
    [TidePoolInitial.fzz, TidePoolProposed.fzz]
2018-04-27 Update code to include LCD
    [TidePoolInitial.fzz, TidePoolProposed.fzz]
2018-05-05 Update code to reflect updated pump set up (on when give 0 volts)
2018-05-07 Update TidePool code to have pump on when write low
2018-05-08 Add schematics and sensor
    [8632200 Kiptopeke, VA.csv]
2018-05-10 Lengthened debounce time to ensure pump will not turn on or off too quickly
2018-05-15 Fix Delay Issue with extreme tides
    [8632200 Kiptopeke Values.csv, 8632200 Kiptopeke, VA.csv]
2018-05-15 Change extreme tidal wait to have the pump on for at least a minute and the pump off for the remanent of the 5 minute time period.
2018-05-16 Update setting LCD and Serial monitor prints to functions including setErrorMessage, setStateMessage, setSensorMessage, and dumpState
2018-05-16 Update PumpLeft and PumpRight variables to PumpFill and PumpDrain respectively
2018-05-16 Update Simplified Tide Pool Diagram to include high and low tide sensors
2018-05-18 Update readme to include description about abstract program switching every 6.5 hours and schematic
    [TidePoolProposed.fzz]
2018-05-24 Update schematic to include high and low sensor bobbers
    [TidePoolProposed.fzz]
2018-06-01 Add Arduino serially communciating with the ESP8266 Wi-Fi sensor to send Tide-Pool height values to Adafrui io on the web
2018-06-01 Update documentation to show that the system is now graphing the tidal level on adafruit io
    [TidePoolInitial.fzz, TidePoolProposed.fzz]
2018-06-21 Update README with components and initial maitenance guide.
    [8632200 Kiptopeke Values.csv]
2018-06-21 Add user manual with description, output (LCD & LED) information, and troubleshooting information.
2018-06-22 Add Arduino Reset Image
2018-06-22 Update Arduino code to restart tide cycle when has integer overflow
